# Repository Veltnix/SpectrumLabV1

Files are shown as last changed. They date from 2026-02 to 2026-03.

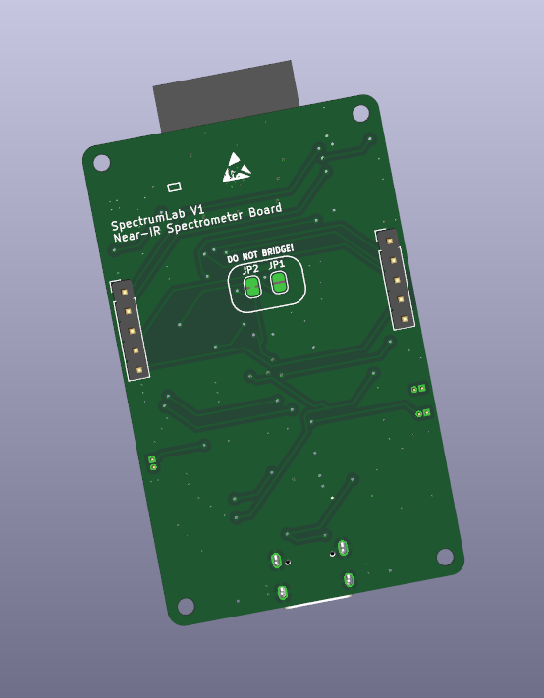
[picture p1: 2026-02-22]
media/kicad3d_back.png

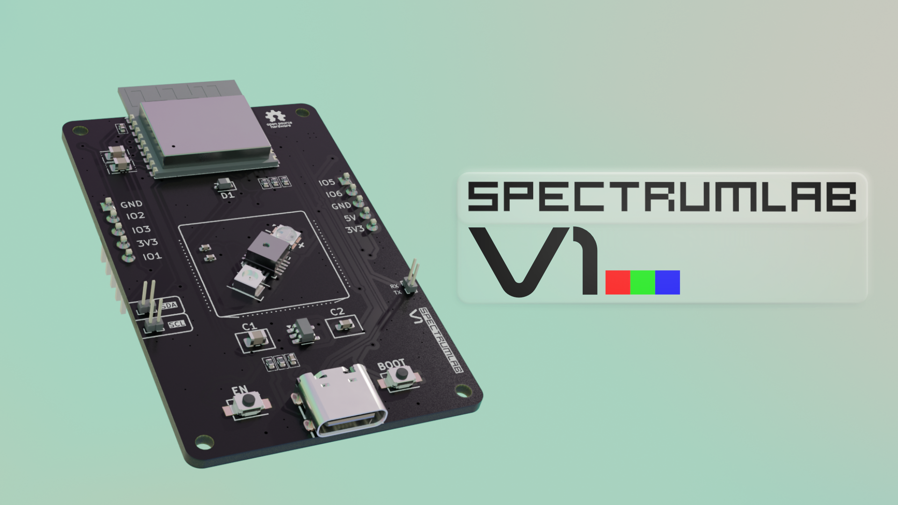
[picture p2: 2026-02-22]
media/render1.png

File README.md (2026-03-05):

<h1 align="center">SpectrumLab V1</h1>

<p align="center">
<b>A Compact VIS–NIR Spectroscopy Development Board powered by ESP32-C3 and AS7263</b>
</p>

<p align="center">

</p>

<hr>

<h2>📌 Overview</h2>

<p>
<b>SpectrumLab V1</b> is a compact VIS–NIR spectroscopy development board built around the ESP32-C3 and the AMS AS7263 spectral sensor.
</p>

<p>
Most spectrometers are big lab instruments. I wanted to see how small and practical a spectral sensing system could be if everything was integrated onto a single embedded board.
</p>

<p>
This project is my attempt to make near-infrared sensing more accessible, portable, and easier to experiment with (and honestly, just more fun to build!) (•‿•)
</p>

<ul>
<li>Compact form factor</li>
<li>USB powered</li>
<li>No moving optics</li>
<li>Wireless capable</li>
<li>Built for experimentation</li>
</ul>

<hr>

<h2>❓ Why I Built This</h2>

<p>
Traditional NIR spectrometers rely on diffraction gratings and mechanical scanning. They are precise, but they are also expensive and not exactly friendly for embedded projects.
</p>

<p>
I wanted something that:
</p>

<ul>
<li>Fits in your hand</li>
<li>Has no moving parts</li>
<li>Can stream data over WiFi</li>
<li>Is easy to integrate into custom hardware projects</li>
</ul>

<p>
SpectrumLab is meant to be both a learning platform and a base for portable sensing ideas such as fruit analysis, material comparison, and reflectance experiments.
</p>

<hr>

<h2>🧠 What This Board Actually Does</h2>

<p>
SpectrumLab measures reflected light intensity at specific wavelengths in the visible to near-infrared range.
</p>

<h3>Main Components</h3>

<ul>
<li><b>ESP32-C3-WROOM-2</b> — Handles processing, USB communication, WiFi and BLE</li>
<li><b>AMS AS7263</b> — 6-channel VIS–NIR spectral sensor</li>
<li><b>128×64 I2C OLED</b> — Displays live spectral data</li>
</ul>

<h3>Spectral Channels</h3>

<ul>
<li>610 nm</li>
<li>680 nm</li>
<li>730 nm</li>
<li>760 nm</li>
<li>810 nm</li>
<li>860 nm</li>
</ul>

<p>
Each channel has about 20 nm bandwidth (FWHM). This does not give a continuous spectrum, but it provides discrete calibrated intensity points that are very useful for classification and trend analysis.
</p>

<h3>How It Measures</h3>

<ol>
<li>The sample is illuminated.</li>
<li>Reflected light enters the AS7263.</li>
<li>The sensor outputs calibrated intensity values.</li>
<li>The ESP32 processes, displays, or streams the data.</li>
</ol>

<p>
Simple, solid-state, and no mechanical scanning (￣▽￣)b
</p>

<hr>

<h2>🔬 What “Compact NIR Spectrometry” Means Here</h2>

<p>
Instead of using a diffraction grating and scanning optics, this board uses a filter-based solid-state spectral sensor.
</p>

<p>
The AS7263 integrates:
</p>

<ul>
<li>Optical filters</li>
<li>On-chip ADC</li>
<li>Digitally calibrated outputs</li>
</ul>

<p>
Because of that, the system:
</p>

<ul>
<li>Has no moving parts</li>
<li>Is physically small</li>
<li>Consumes less power</li>
<li>Is much easier to embed into custom hardware</li>
</ul>

<p>
It is not a lab-grade continuous spectrometer. It is a compact, embedded-friendly spectral measurement platform designed for experimentation and real-world integration.
</p>

<hr>

<h2>🧩 PCB</h2>

<p align="center">


</p>

<p>
Design goals:
</p>

<ul>
<li>2-layer compact PCB</li>
<li>Fully surface-mount</li>
<li>USB-C powered (5V to 3.3V regulation)</li>
<li>Dedicated I2C breakout pins</li>
<li>Debug jumper bridges</li>
</ul>

<hr>

<h2>📐 Schematics</h2>

<p align="center">

</p>

<hr>

<h2>💻 Example Code (SSD1306 Interface)</h2>

<pre><code>
#include &lt;Wire.h&gt;
#include &lt;Adafruit_SSD1306.h&gt;
#include "AS726X.h"

#define SDA_PIN 8
#define SCL_PIN 9

#define SCREEN_WIDTH 128
#define SCREEN_HEIGHT 64

Adafruit_SSD1306 display(SCREEN_WIDTH, SCREEN_HEIGHT, &Wire, -1);
AS726X sensor;

void setup() {
  Serial.begin(115200);
  Wire.begin(SDA_PIN, SCL_PIN);

  if (!display.begin(SSD1306_SWITCHCAPVCC, 0x3C)) {
    while (1);
  }

  if (!sensor.begin()) {
    while (1);
  }

  sensor.setGain(AS726X_GAIN_16X);
  sensor.setIntegrationTime(50);
  sensor.enableBulb(AS726X_LED_IR);
}

void loop() {
  sensor.takeMeasurements();
  delay(500);
}
</code></pre>

<hr>

<h2>⭐ Notable Features</h2>

<ul>
<li>ESP32-C3-WROOM-2 with WiFi and BLE</li>
<li>610 nm to 860 nm spectral coverage</li>
<li>~20 nm channel bandwidth</li>
<li>USB-C connectivity</li>
<li>External I2C header</li>
<li>Compact and portable</li>
</ul>

<hr>

<h2>💰 BOM & Manufacturing</h2>



<hr>

<h2>🚀 Potential Applications</h2>

<ul>
<li>Fruit ripeness estimation</li>
<li>Material comparison</li>
<li>Reflectance experiments</li>
<li>Educational spectroscopy demos</li>
<li>Embedded ML classification</li>
</ul>

<hr>

<h2>🛠 Programs Used</h2>

<ul>
<li>KiCad (Schematics & PCB)</li>
<li>Fusion 360 (STEP modeling)</li>
<li>Blender (3D render)</li>
</ul>

<hr>

<h2>🛡 License</h2>

<p>MIT License</p>

<hr>

<h2>❤️ Support</h2>

<p>
Support this project on Hack Club:<br>
<a href="https://blueprint.hackclub.com/projects/12271">
https://blueprint.hackclub.com/projects/12271
</a>
</p>

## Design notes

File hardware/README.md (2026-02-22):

## SpectrumLab V1

## JUMPER
JP1 ... VBUS = 5V jumper (Default: not connected): Connecting this disables the protective SBD between USB and external power supply. To eliminate the voltage drop due to SBD and output the voltage input from USB as it is to 5V, connect this jumper. Note that shorting this pin will increase current consumption by about 0.1mA due to the pull-down resistor on the CC pin.

JP2 ... 5V -> 3.3V jumper (Default: connected): Connection of the external power supply terminal (5V pin) to the power input terminal to the ESP32-C3. Disconnect when suppressing regulator quiescent current.

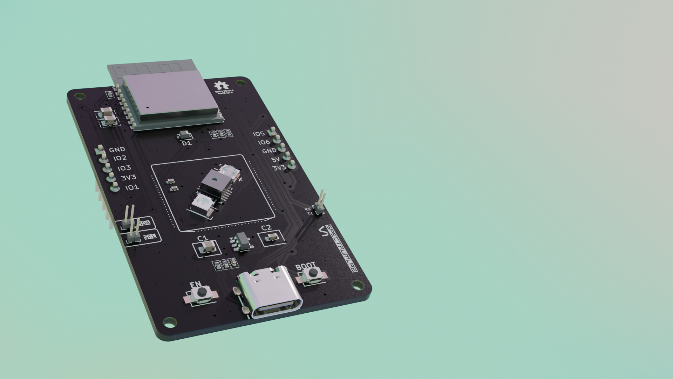
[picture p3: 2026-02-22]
media/spectrumlab.png

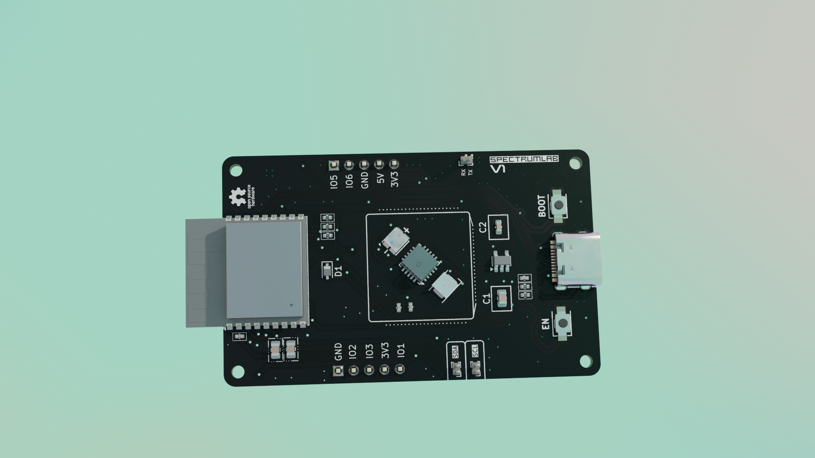
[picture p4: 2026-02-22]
media/renderhorizontal.png

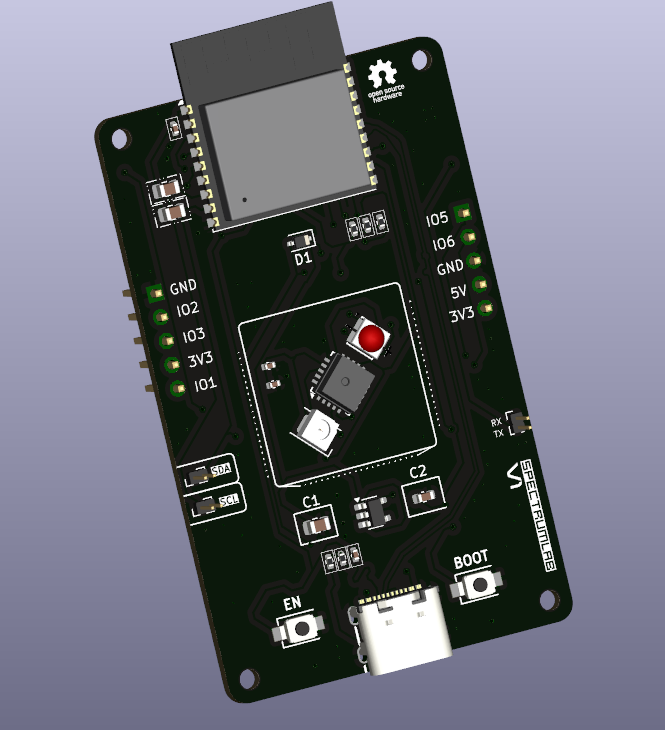
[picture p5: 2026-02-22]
media/kicad3d_front.png

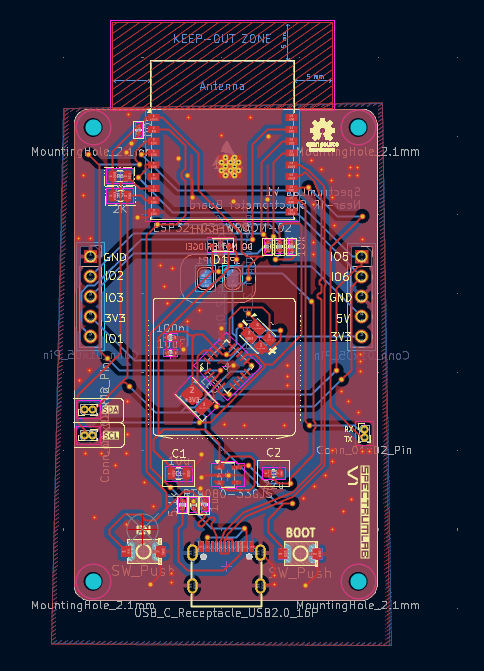
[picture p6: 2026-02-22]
media/pcb.png

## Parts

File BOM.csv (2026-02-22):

Name | Cost | Source
JLCPCB Parts Assembly | 86.2 | JLCPCB
PCB + Shipping | 21 | JLCPCB
PIN Headers | 4 | Tokopedia
Total | 112 | -

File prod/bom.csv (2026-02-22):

Designator | Footprint | Quantity | Value | LCSC Part #
BOOT1, EN1 | TS-1088-AR02016 | 2 | SW_Push | C115360
C1 | 0805 | 1 | 10u | C15850
C2 | 0603 | 1 | 22u | C59461
C3 | 0402 | 1 | 1u | C52923
C4, C5 | 0402 | 2 | 100n | C1525
C6 | 0402 | 1 | 10uF | C1525
D1 | D_SOD-323 | 1 | 1N5819WS | C191023
D3 | LED_Everlight-SMD3528_3.5x2.8mm_67-21ST | 1 | LED | C2830527
D5 | LED-SMD_4P-L3.2-W3.0_RS6694-S820B1 | 1 | ~ | C19944431
J1 | USB-C_SMD-TYPE-C-31-M-12 (JLC) | 1 | USB_C_Receptacle_USB2.0_16P | C2988369
J2, J3 | PinHeader_1x05_P2.54mm_Vertical | 2 | Conn_01x05_Pin
J4, J5, J6 | PinHeader_1x02_P1.00mm_Vertical | 3 | Conn_01x02_Pin
R1, R2 | 0402 | 2 | 5.1k | C25905
R3, R4, R5 | 0402 | 3 | 10k | C25744
R6, R7 | 0805 | 2 | 2K | C17604
U1 | ESP32-C3-WROOM-02 | 1 | ESP32-C3-WROOM-02 | C2934560
U2 | AMS_LGA-20_4.7x4.5mm_P0.65mm | 1 | AS7263 | C2655137
U3 | SOT-23-5 | 1 | RT9080-33GJ5 | C841192

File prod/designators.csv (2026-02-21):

BOOT1:1
C1:1
C2:1
C3:1
C4:1
C5:1
C6:1
D1:1
D3:1
D5:1
EN1:1
G***:2
J1:1
J2:1
J3:1
J4:1
J5:1
J6:1
JP1:1
JP2:1
R1:1
R2:1
R3:1
R4:1
R5:1
R6:1
R7:1
REF**:4
U1:1
U2:1
U3:1

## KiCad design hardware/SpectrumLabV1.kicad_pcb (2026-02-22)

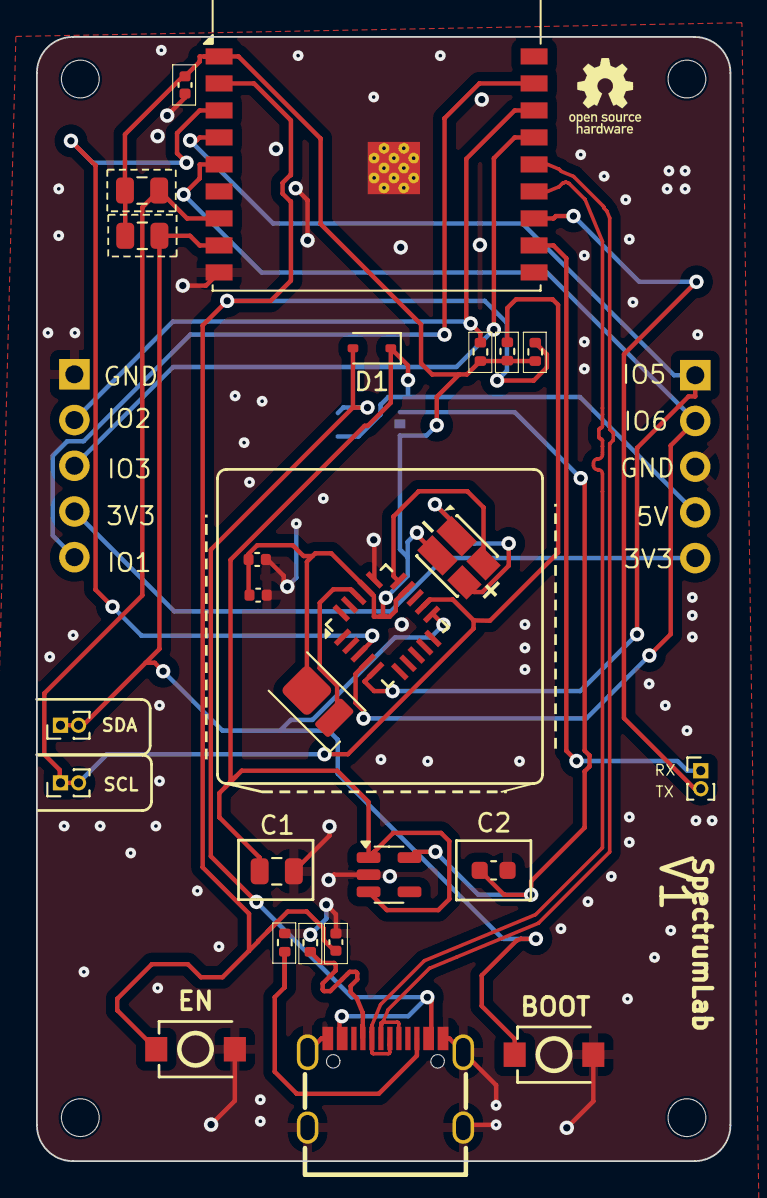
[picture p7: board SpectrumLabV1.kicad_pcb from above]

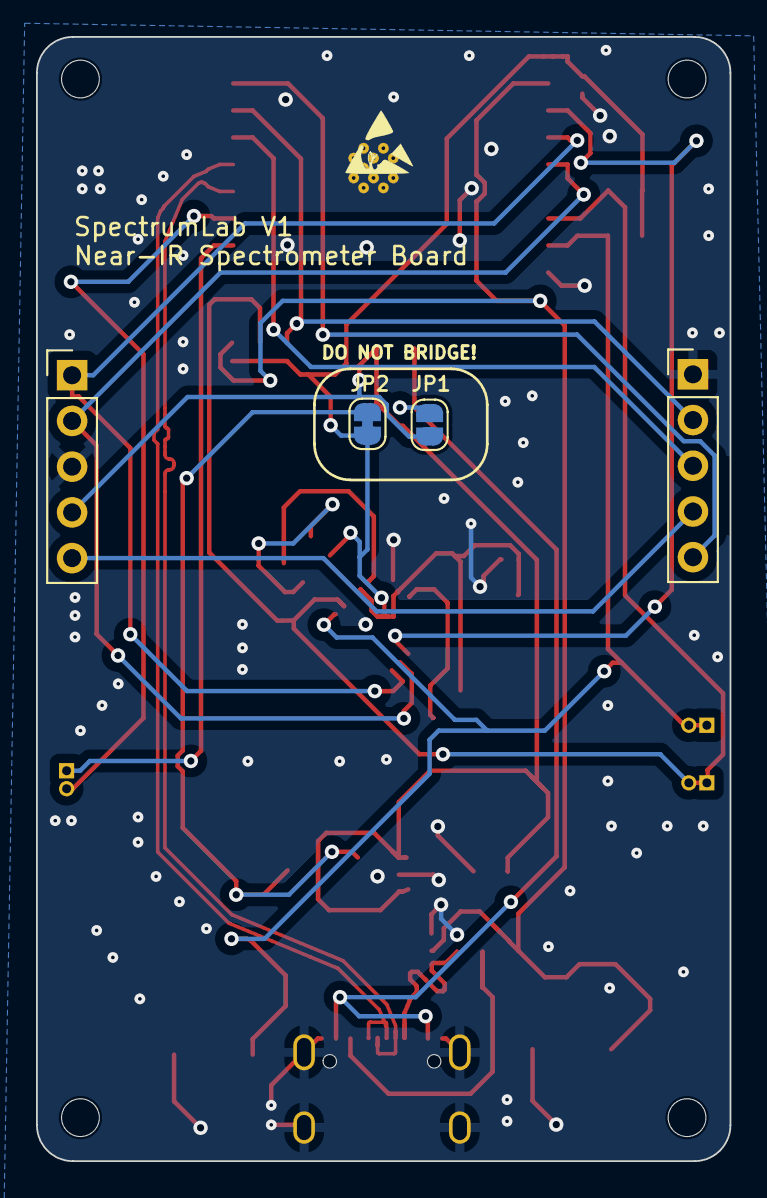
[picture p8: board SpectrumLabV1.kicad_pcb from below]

Board: 2 copper layers, 38.5 x 62.5 mm, 29 parts (4 on the bottom side), 24 nets.

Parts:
BOOT1: SW_Push; TS-1088-AR02016
C1: 10u; C_0805_2012Metric
C2: 22u; C_0603_1608Metric
C3: 1u; C_0402_1005Metric
C4, C5: 100n; C_0402_1005Metric
C6: 10uF; C_0402_1005Metric
D1: 1N5819WS; D_SOD-323
D3: LED; LED_Everlight-SMD3528_3.5x2.8mm_67-21ST
D5: LED-SMD_4P-L3.2-W3.0_RS6694-S820B1
EN1: SW_Push; TS-1088-AR02016
J1: USB_C_Receptacle_USB2.0_16P; USB-C_SMD-TYPE-C-31-M-12 (JLC)
J2, J3: Conn_01x05_Pin; PinHeader_1x05_P2.54mm_Vertical
J4, J5, J6: Conn_01x02_Pin; PinHeader_1x02_P1.00mm_Vertical
JP1: SolderJumper_2_Open; SolderJumper-2_P1.3mm_Open_RoundedPad1.0x1.5mm
JP2: SolderJumper_2_Bridged; SolderJumper-2_P1.3mm_Bridged_RoundedPad1.0x1.5mm
R1, R2: 5.1k; R_0402_1005Metric
R3, R4, R5: 10k; R_0402_1005Metric
R6, R7: 2K; C_0805_2012Metric
U1: ESP32-C3-WROOM-02
U2: AS7263; AMS_LGA-20_4.7x4.5mm_P0.65mm
U3: RT9080-33GJ5; SOT-23-5

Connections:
+3V3: C4.2, C5.2, C6.2, D3.2 (A), D5.2, JP2.2 (B), R3.1, R4.1, R5.1, R6.1, R7.1, U1.1 (3V3), U2.14 (VDD), U2.17 (VDD)
+5V: C1.2, D1.1 (K), J3.4, JP1.2 (B), U3.1 (IN), U3.3 (EN)
/3V3: J2.4, J3.5
/EN: C3.1, EN1.1, R5.2, U1.2 (EN/CHIP_PU)
/IO1: J2.5, U1.17 (GPIO1/ADC1_CH1/XTAL_32K_N)
/IO2: J2.2, R3.2, U1.16 (GPIO2/ADC1_CH2)
/IO3: J2.3, U1.15 (GPIO3/ADC1_CH3)
/IO4: U1.3 (GPIO4/ADC1_CH4), U2.3 (SCK)
/IO5: J3.1, U1.4 (GPIO5/ADC2_CH0), U2.5 (MISO)
/IO6: J3.2, U1.5 (GPIO6), U2.4 (MOSI)
/IO18: J1.A7 (D-), J1.B7 (D-), U1.13 (GPIO18/USB_D-)
/IO19: J1.A6 (D+), J1.B6 (D+), U1.14 (GPIO19/USB_D+)
/RXD: J6.1, U1.11 (GPIO20/U0RXD)
/TXD: J6.2, U1.12 (GPIO21/U0TXD)
GND: BOOT1.2, C1.1, C2.2, C3.2, C4.1, C5.1, C6.1, EN1.2, J1.A1 (GND), J1.A12 (GND), J1.B1 (GND), J1.B12 (GND), J1.S1 (SHIELD), J2.1, J3.3, R1.2, R2.1, U1.9 (GND), U1.19 (GND), U2.16 (GND), U3.2 (GND)
unnamed: D3.1 (K), U2.18 (LED_IND)
unnamed: D5.1, D5.4
unnamed: J1.A5 (CC1), R1.1
unnamed: J1.B5 (CC2), R2.2
unnamed: C2.1, JP2.1 (A), U3.5 (OUT)
unnamed: D5.3, U2.15 (LED_DRV)
SCL: J5.1, J5.2, R4.2, R6.2, U1.7 (GPIO8), U2.12 (TX/SDA_S)
SDA: BOOT1.1, J4.1, J4.2, R7.2, U1.8 (GPIO9), U2.11 (RX/SCL_S)
VBUS: D1.2 (A), J1.A4 (VBUS), J1.A9 (VBUS), J1.B4 (VBUS), J1.B9 (VBUS), JP1.1 (A)

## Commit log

2026-02-21 Add production files
    [bom.csv, designators.csv, positions.csv]
2026-02-22 Replaced Prod File with the corrected BOM and Footprint
    [bom.csv]
2026-02-22 Add Media & Hardware
    [AS7263.kicad_sch, BOM.csv, Header.kicad_sch, SpectrumLabV1.kicad_pcb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]
2026-02-22 Updated bom.csv on prod
    [bom.csv]
2026-02-22 Align PCB image in README
    Align PCB image to the left in README.
2026-02-22 Update README with images and PCB details
    Added images and updated PCB section in README.
